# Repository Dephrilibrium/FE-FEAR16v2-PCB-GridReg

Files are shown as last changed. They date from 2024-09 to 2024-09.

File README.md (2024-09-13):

# FEAR-Grid Regulation
This repository contains the KiCAD-design files for a shield of the F(ield) E(mission) A(rray) R(egulation) current control circuit.

**Note:** This project is part of the SubModule-repository [FE-FEAR16v2][FE-FEAR16v2-SubmoduleRepo], where you can find sub-repositories for other shield-PCBs, mainboard-PCB and the firmware.

# Description
The name "grid regulation" comes from the original main purpose of regulating the potential of the extraction grid (extraction voltage) of a field emission array (FEA = cathode) based on the current through the cathode. However, it can be used in all cases where a potential needs to be regulation (Grid-input) based on the current-flow through the device under test which can be connected on a separate measurement-input (FEA-input). During active regulation this shield acts like a current-source/-sink.

- The shield itself takes 1 DAC-output voltage (V~Ctrl~ = 0..10V) to adjust the current control.
- The A(mperemeter) is actually a shunt-resistor which defines the measurable current range. A 1MΩ for instance yields a range from 0.31 nA (resolution) to 10 µA, whereby its wisely to keep the current slightly below as 10 µA is the absolute maximum measurable value.
- The V(oltmeter) measures the internal voltage-drop over the FET.

**Note:** Both, A and V use potentiometers to adjust their feedback-loop amplification. Due to tolerances on all the parts, its recommended to use a shield only at a specific mainboard and a specific channel-position at which the boards were calibrated.

**Principle of the cathode regulation:**
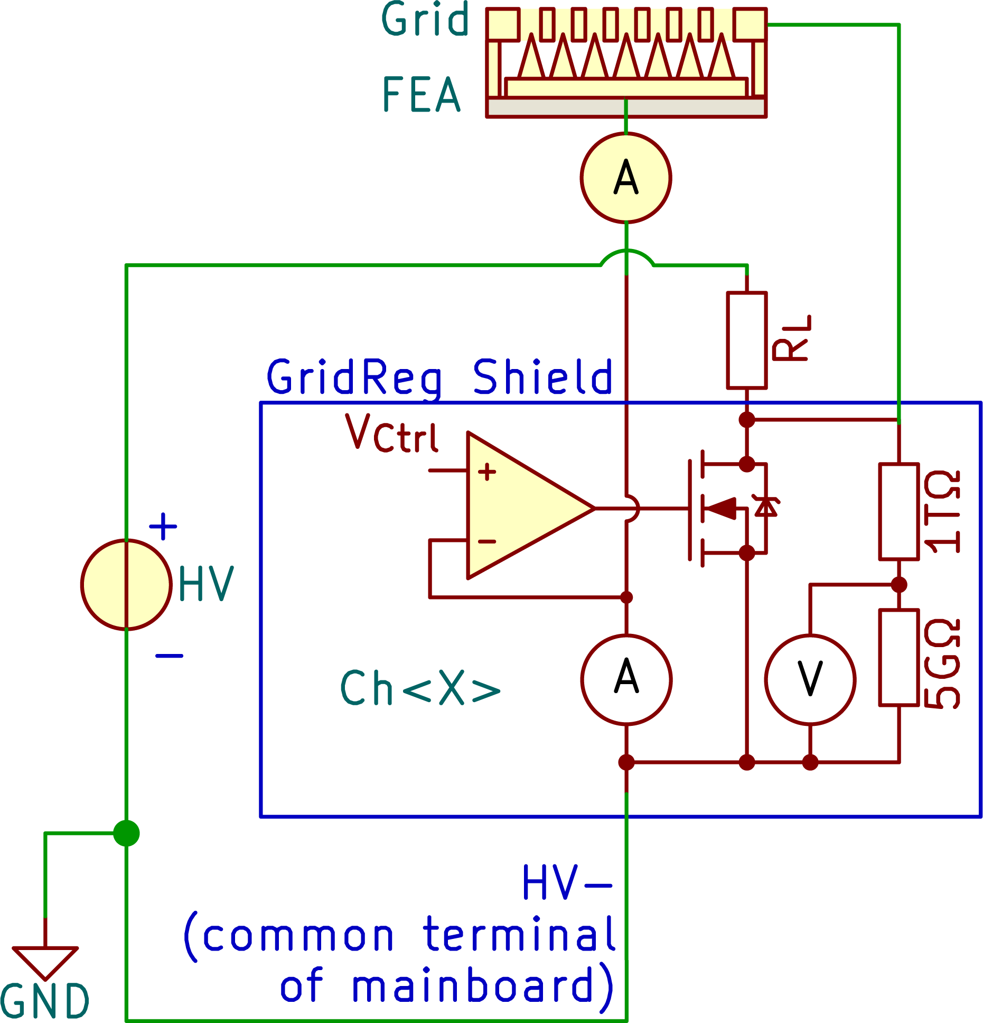
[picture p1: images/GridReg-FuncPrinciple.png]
Principle of the regulation


# HowTo to connect (samples and for calibration)
1. Place a shield on a mainboard/channel-slot.

2. Calibration: continue with step 3., otherwise go to 5.

3. Calibrate V~Shnt~ (FEA-Input)

    1. Connect the positive supply of a voltage source (needs to supply voltages up to 10V) to the FEA-input via an amperemeter (see figure above) and the negative supply (GND) to the HV- input. Note that amperemeter for fine-tuning the V~Shnt~ measurement (FEA-Input) is located between FEA-Input and FEA for circuitry reasons. As over the GridReg-Shield a voltage-drop occurs (up to 10V), the amperemeter needs to be able to withstand a few volts between measurement input and earth.

    2. Apply a voltage to the input (e.g. 9V).

    3. Adjust the current gain potentiometer, so that the measured ADC value divided by the shunt-resistance is equal to the amperemeter-value (V~Shnt~/R~Shunt~ = I~Amperemeter~)

4. Calibrate V~Drp~ (Grid-Input)

    1. Make sure, the FEA-Input connection of 3.i. above was made.

    2. Connect a high voltage-supply (via a Load-Resistor R~L~) to the Grid-Supply-Input (for further explanations see note below) and apply a high voltage (e.g. 1kV).

    3. Adjust the FEA-input voltage of 3.ii., so that the NFET blocks the current flow (Grid-Potential should increase to 1kV). If the FEA-Input voltage has to be higher or lower than V~Ctrl~ depends if you use the additional inverter-option which can be connected to the NFET-gate on the PCB.

    4. Adjust the voltage-drop gain potentiometer. The board projects a voltage range of &pm;1500V into a range of &pm;10V using a voltage divider with huge resistance values. Example for positive voltage:
    1500V * 5GΩ / 1005GΩ * Gain = 7.462..V * Gain = 10V
    Gain = 10V / 7.462..V = 1.34

5. Connect your FEA on the shield's FEA-Input screw terminal, the extraction grid to the the most negative supply to to HV- (which is the mainboard's common-terminal).

**Note:**
- The load-resistor R~L~ is a simple approach of increasing the voltage on the Grid-Input. This is because the high voltage of up to 1500V makes a  performant half-bridge design (regulated PFET instead of R~L~) tricky to realize. Its also noteworthy that R~L~ creates an asymmetric time-behaviour in charging and discharging the voltage of the extraction grid, and depends on the speeds your applications require.
- The FEAR command-documentation can be found in the firmware-repository (see [FE-FEAR16v2 Submodule-Repo][FE-FEAR16v2-SubmoduleRepo]).

[FE-FEAR16v2-SubmoduleRepo]: https://github.com/Dephrilibrium/FE-FEAR16v2

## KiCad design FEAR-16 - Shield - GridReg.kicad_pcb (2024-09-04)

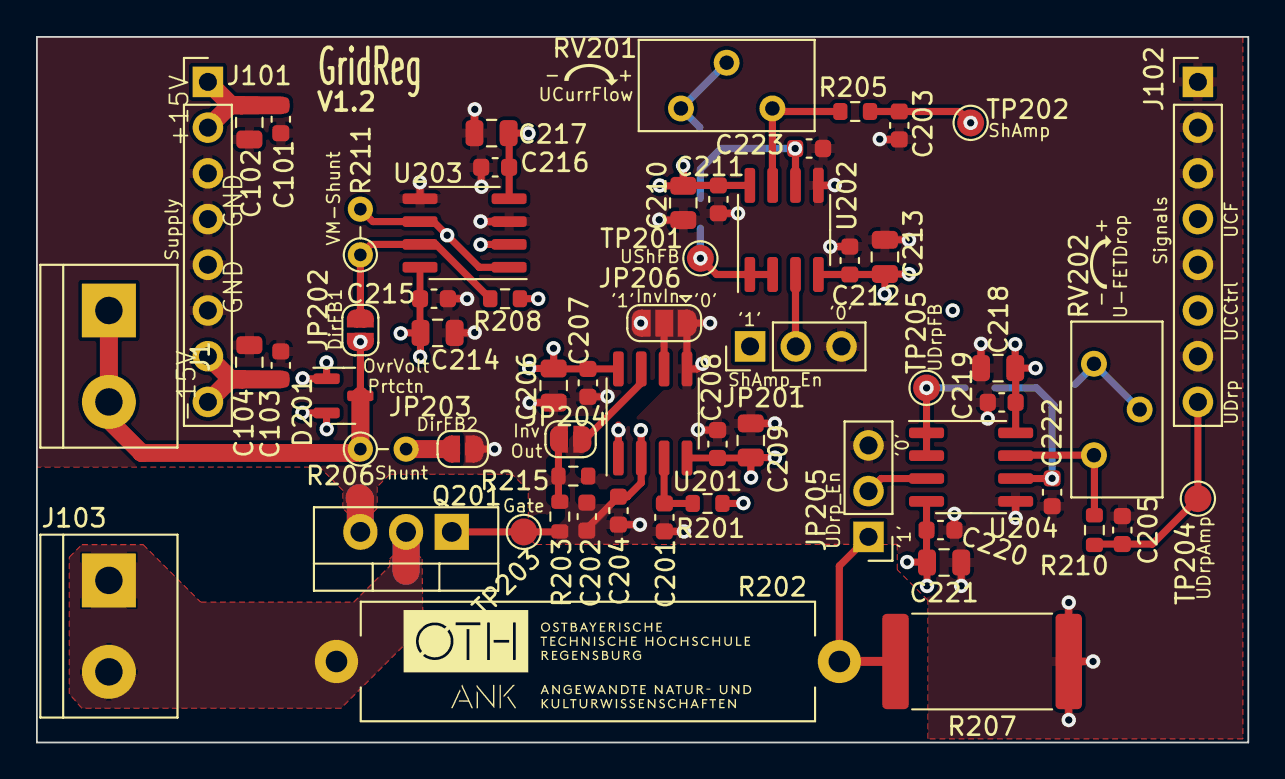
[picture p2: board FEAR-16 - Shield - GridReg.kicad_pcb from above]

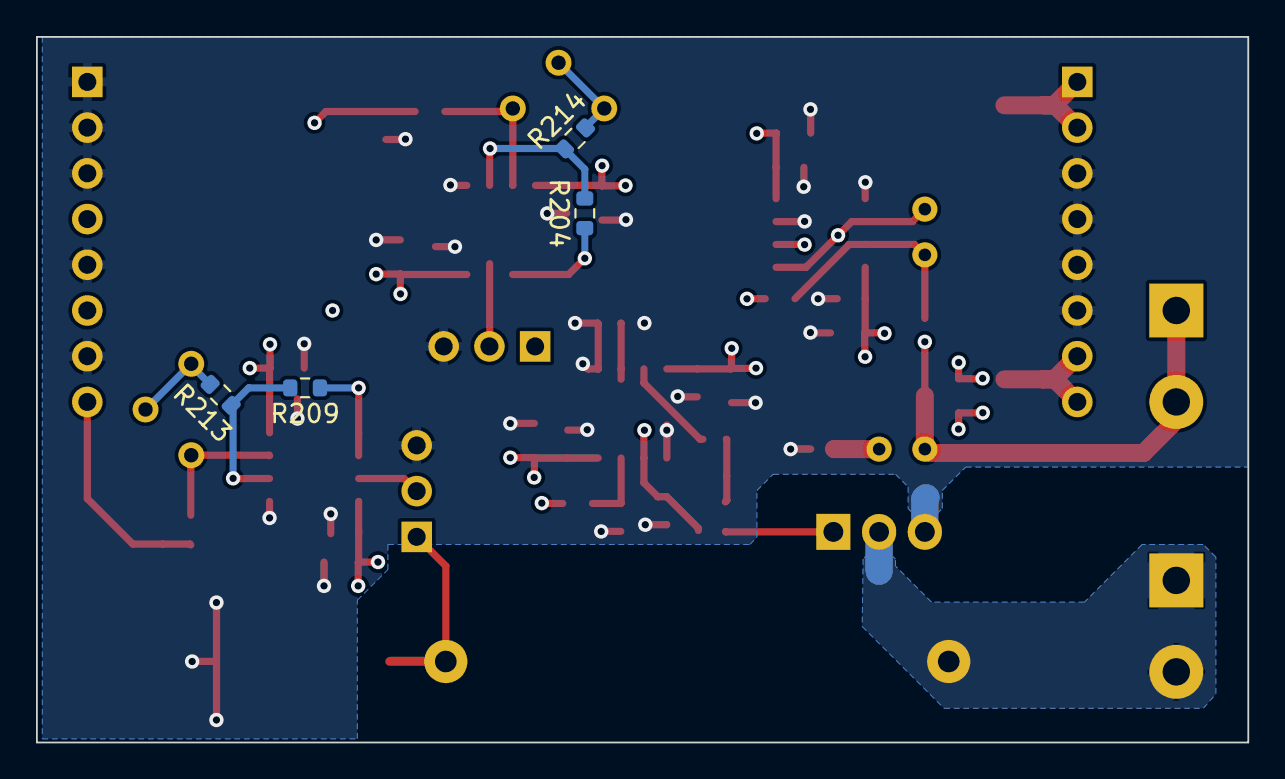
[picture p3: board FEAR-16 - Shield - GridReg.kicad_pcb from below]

Board: 4 copper layers, 67.3 x 39.2 mm, 64 parts (4 on the bottom side), 28 nets.

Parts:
C101, C103, C202, C207, C208, C211, C212, C215, C216, C219, C220: 100n/25V; C_0603_1608Metric
C102, C104, C206, C209, C210, C213, C214, C217, C218, C221: 10µ/25V; C_0805_2012Metric
C201: 1n/25V; C_0603_1608Metric
C203, C205: 470p/25V; C_0603_1608Metric
C204: 1n/25V (opt.); C_0603_1608Metric
C222, C223: 220n/25V; C_0603_1608Metric
D201: BAV99; SOT-23
J1, J103: Channel-In; TerminalBlock_bornier-2_P5.08mm
J101: Supply; PinHeader_1x08_P2.54mm_Vertical
J102: Signals; PinHeader_1x08_P2.54mm_Vertical
JP201: ShAmp_En; PinHeader_1x03_P2.54mm_Vertical
JP202: DirFB1; SolderJumper-2_P1.3mm_Open_RoundedPad1.0x1.5mm
JP203: DirFB2; SolderJumper-2_P1.3mm_Open_RoundedPad1.0x1.5mm
JP204: Invert_{Out}; SolderJumper-2_P1.3mm_Open_RoundedPad1.0x1.5mm
JP205: UDrp_En; PinHeader_1x03_P2.54mm_Vertical
JP206: Invert_{In}; SolderJumper-3_P1.3mm_Open_RoundedPad1.0x1.5mm
Q201: NDFPD1N150CG; TO-220-3_Vertical
R201: 1k; R_0603_1608Metric
R202: 1T/5%; R_Axial_Power_L25.0mm_W6.4mm_P27.94mm
R203: 220R; R_0603_1608Metric
R204, R205, R209, R210, R213, R214: 100k; R_0603_1608Metric
R206: Shunt; R_Axial_DIN0204_L3.6mm_D1.6mm_P2.54mm_Vertical
R207: 5G/5%; R_4020_10251Metric
R208: 220R (opt); R_0603_1608Metric
R211: VM-Shunt; R_Axial_DIN0204_L3.6mm_D1.6mm_P2.54mm_Vertical
R215: 1Meg; R_0603_1608Metric
RV201, RV202: 50k; Potentiometer_Bourns_3296Y_Vertical
TP201: UShFB; TestPoint_Pad_D1.5mm
TP202: ShAmp; TestPoint_Pad_D1.5mm
TP203: Gate; TestPoint_Pad_D1.5mm
TP204: UDrpAmp; TestPoint_Pad_D1.5mm
TP205: UDrpFB; TestPoint_Pad_D1.5mm
U201, U202, U203, U204: OPA2156xD; SOIC-8_3.9x4.9mm_P1.27mm

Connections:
+15V: C101.2, C102.2, C206.2, C207.2, C210.2, C211.2, C214.2, C215.2, C218.2, C219.2, D201.2 (A), J101.1, J101.2, U201.8 (V+), U202.8 (V+), U203.8 (V+), U204.8 (V+)
-15V: C103.1, C104.1, C208.2, C209.2, C212.2, C213.2, C216.2, C217.2, C220.2, C221.2, D201.1 (K), J101.7, J101.8, U201.4 (V-), U202.4 (V-), U203.4 (V-), U204.4 (V-)
/CathIn: D201.3 (K), J1.1, J1.2, JP202.2 (B), R206.1, U203.2 (-)
/Channel/UDrp: JP205.1 (A), R202.1, R207.2
/Channel/USh: C202.1, C204.2, JP201.1 (A), R208.2, U201.2 (-)
/GridIn: J103.1, J103.2, Q201.2 (D), R202.2
/UCurrCtrl: J102.6, R201.1
/UCurrFlow: C203.2, J102.4, R205.1, TP202.1
/UFETDrop: C205.2, J102.8, R210.1, TP204.1
GND: C101.1, C102.1, C103.2, C104.2, C201.2, C203.1, C204.1, C205.1, C206.1, C207.1, C208.1, C209.1, C210.1, C211.1, C212.1, C213.1, C214.1, C215.1, C216.1, C217.1, C218.1, C219.1, C220.1, C221.1, C222.1, C223.1, J101.3, J101.4, J101.5, J101.6, J102.1, J102.2, J102.3, J102.5, J102.7, JP201.3 (B), JP203.2 (B), JP205.3 (B), JP206.1 (A), Q201.3 (S), R207.1, U201.5 (+), U202.5 (+), U203.3 (+), U203.5 (+), U204.5 (+)
unnamed: JP201.2 (C), U202.3 (+)
unnamed: JP202.1 (A), R208.1, R211.1, U203.7
unnamed: JP203.1 (A), R206.2, R211.2, U203.1, U203.6 (-)
unnamed: JP204.1 (A), R203.1, R215.2
unnamed: JP204.2 (B), U201.7
unnamed: JP205.2 (C), U204.3 (+)
unnamed: C202.2, JP206.3 (B), R215.1, U201.1
unnamed: JP206.2 (C), U201.6 (-)
unnamed: Q201.1 (G), R203.2, TP203.1
unnamed: R205.2, RV201.3, U202.7
unnamed: R210.2, RV202.3, U204.7
unnamed: R213.2, RV202.1, RV202.2
unnamed: R214.2, RV201.1, RV201.2
unnamed: C201.1, R201.2, U201.3 (+)
unnamed: R204.1, TP201.1, U202.1, U202.2 (-)
unnamed: C223.2, R204.2, R214.1, U202.6 (-)
unnamed: R209.1, TP205.1, U204.1, U204.2 (-)
unnamed: C222.2, R209.2, R213.1, U204.6 (-)

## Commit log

2024-09-04 Added option to invert FET-Gate voltage
    Added JP206 (3Pad Solder Jumper) and JP204 (2Pad Solder Jumper)
    These using the, until now, unused second OpAmp of U201.
    --> Jumpers that allow to invert the FET-Gate Voltage
    FET-Gate Voltage acts as Grid-Regulation (inverting):
    - Close JP206 Pins 2 with 3
    - Close JP204
    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
    [FEAR-16 - Shield - GridReg.kicad_pcb, FEAR-16 - Shield - GridReg.kicad_sch, OneChannel.kicad_sch, principle_circuit.kicad_sch]
2024-09-12 Added comments on UFET feedback loop
    [FEAR-16 - Shield - GridReg.kicad_sch, OneChannel.kicad_sch]
